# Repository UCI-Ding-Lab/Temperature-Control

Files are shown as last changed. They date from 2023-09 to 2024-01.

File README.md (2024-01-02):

# Ding Temperature Control
An accurate, customizable, and cost-effective temperature control system.
Please reach out to [UCI Ding Lab](https://www.ding.eng.uci.edu) for any questions or requests. 

The temperature control system is designed to maintain a stable temperature from room temperature to 60 °C within 0.06 °C. On the aluminum target block, two adhesive polyimide heating elements and two temperature sensors are attached on the side. These sensors and heating elements are connected to an Arduino Nano which controls the temperature output with an external 24V power supply using the PID algorithm. 

This GitHub repository includes the PCB KiCad and Gerber files, PCB enclosure Fusion 360 and STL files, and Arduino code.

### Major steps to build the system.
Protocol Graphical Abstract

## PCB
The PCB is designed in KiCad 6.0, in which users can edit the layout for free. It is a 2-layer board with all through-hole components. 
The top layer is a +5V plane and the back layer is a ground plane. 
It houses the Arduino Nano, female headers, DC barrel jack, and screw terminal jack.

### Layout of the PCB
Ding Temperature Control PCB Layout

### KiCad model of the PCB
Ding Temperature Control PCB Transparent

## Enclosure
The enclosure is designed in Fusion 360 with a top and bottom piece. It is designed to be printed on a 3D printer with PLA and without any support. 
It contains M3 threaded inserts to connect the PCB, LCD, and buck converter. 

A Fusion 360 model of the enclosure.
Ding Temperature Control Housing

## Arduino Code
The Arduino Nano on the PCB reads the temperature sensors and calculates the heating power to reach the target temperature with the PID algorithm. 
Then, a PWM signal is sent to the MOSFET with the heating elements to heat the target block.
The PID algorithm is implemented from [QuickPID](https://github.com/Dlloydev/QuickPID).

## Example Data
The temperature recording of 4 trials has been provided in an Excel workbook. 

Note: The probe temperature sensor sometimes read -127 °C. This is an expected behavior. The PID algorithm omits the sensor reading and uses the previous average temeprature to calculate power output.



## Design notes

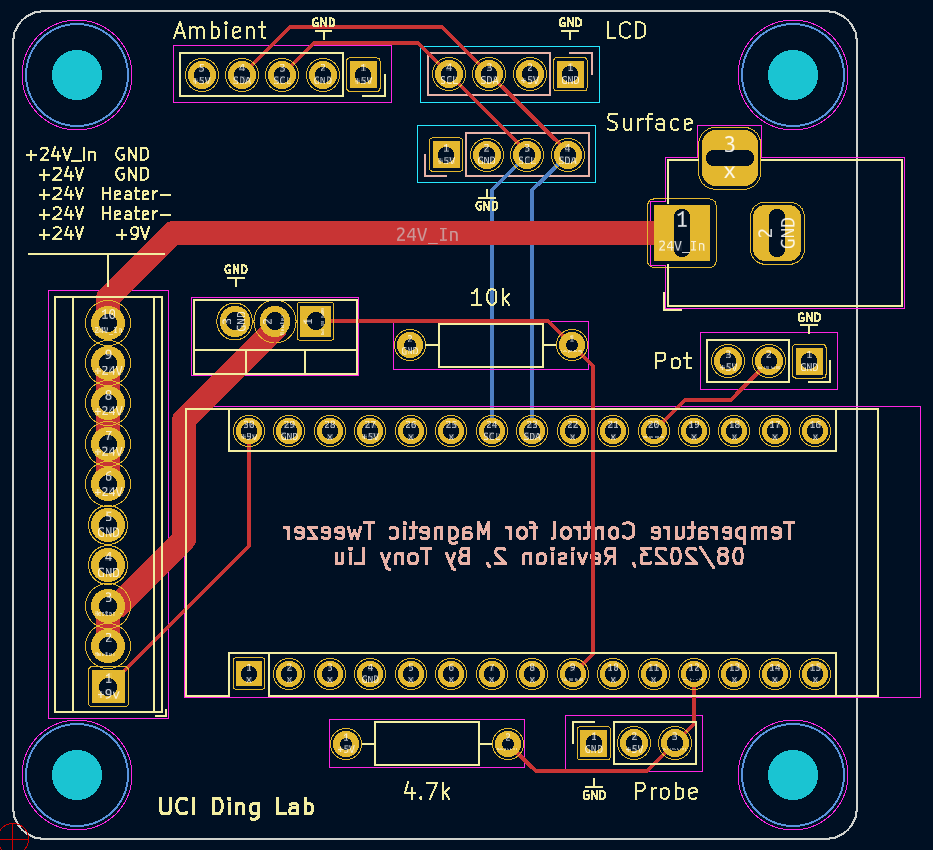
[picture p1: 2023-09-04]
PCB/Ding Temperature Control PCB Layout.png

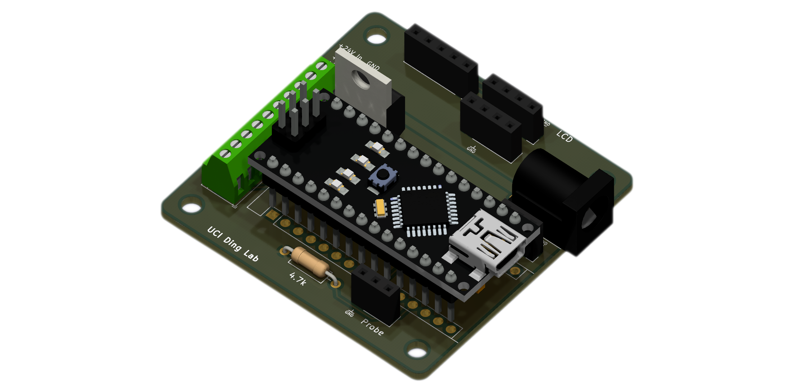
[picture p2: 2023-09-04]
PCB/Ding Temperature Control PCB Transparent.png

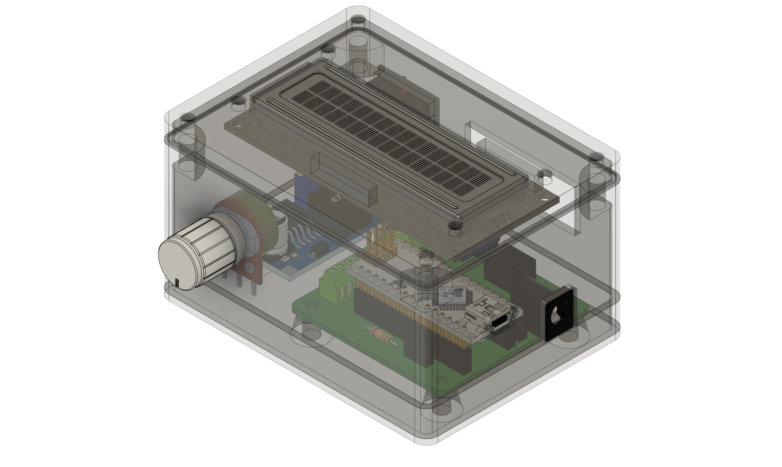
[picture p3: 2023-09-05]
Enclosure/Ding Temperature Control Housing.png

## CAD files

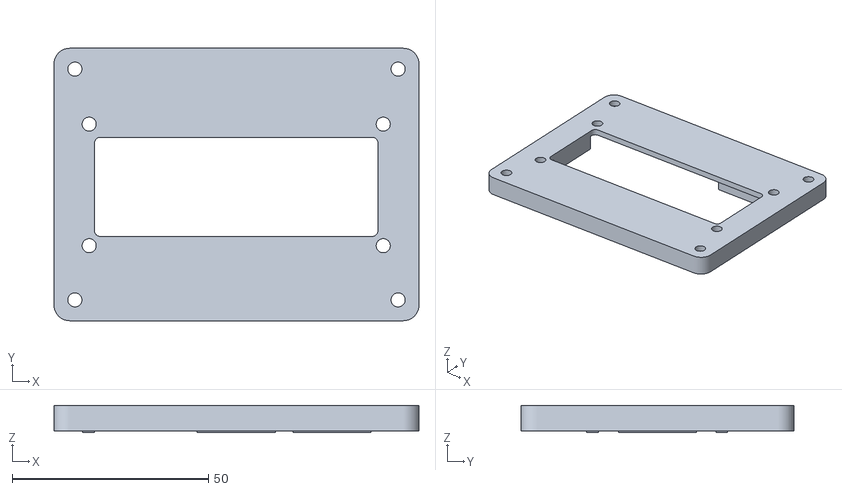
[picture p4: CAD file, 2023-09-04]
Enclosure/Enclosure Top.stl
93.1 x 69.5 x 6.90

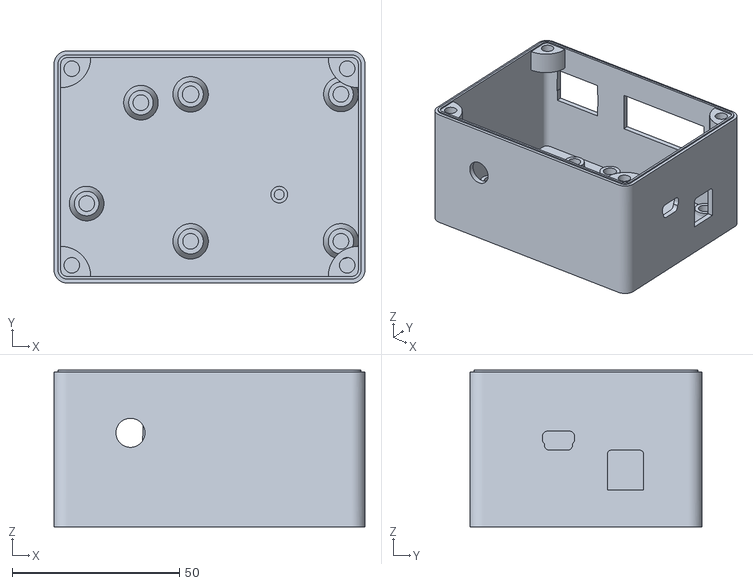
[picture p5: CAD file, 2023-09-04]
Enclosure/Enclosure Bottom.stl
93.1 x 69.5 x 46.9

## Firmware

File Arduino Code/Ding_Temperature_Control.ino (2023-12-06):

/********************************************************
   PID Temperature Control for Microscopes, Microfluidic Chambers, and Custom Incubators
   By: Tony Liu @ Ding Lab
 ********************************************************/

// Include libraries for sensors, LCD, and PID
#include <OneWire.h>
#include <DallasTemperature.h>
#include <Wire.h>
#include "Adafruit_MCP9808.h"
#include <LiquidCrystal_I2C.h>
#include <QuickPID.h>

// Declare physical pin numbers connected to the components
const int PROBEPIN = 9;
const int HEATERPIN = 6;
const int TARGETPIN = 1;

// Declare tempearture variables
float targetTemp, Input, Output;
double probeTemp, mcpTemp, mcpTemp2, avgTemp;

// PID constants; change these according to your setup in step 4
float Kp = 505, Ki = 62, Kd = 92;

// Constructors for sensors
OneWire oneWire(PROBEPIN);
DallasTemperature probe(&oneWire);
LiquidCrystal_I2C lcd(0x27,20,4);
Adafruit_MCP9808 mcp = Adafruit_MCP9808();
Adafruit_MCP9808 mcp2 = Adafruit_MCP9808();

// Create PID object from QuickPID library by David Lloyd 
QuickPID myPID(&Input, &Output, &targetTemp);

// Reads potentiometer (temperature control knob) input and converts to 20-60 Degree for the target temperature
void changeTargetTemp()
{
  // Read potentiometer input from 0 to 1023
  int targetInput = analogRead(TARGETPIN);

  // Converts potentiometer input to 20-60 degree target temperature
  targetTemp = map(targetInput, 0, 1023, 20, 60);
}

//Reads all temperature sensors and potentiometer
void readInput() 
{
  // Reads the target temperature from the potentiometer
  changeTargetTemp();

  // Prints the target temperature to the serial monitor
  Serial.print("Target:");
  Serial.print(targetTemp);
  Serial.print(" ");

  // Prints the target temperature to the top right of the LCD
  lcd.setCursor(9, 0);
  lcd.print("T:");
  lcd.print(targetTemp, 2);

  // Updates the temperature reading from the probe sensor, prevents unstable -127 readings
  probe.requestTemperatures(); 
  float probeReading = probe.getTempCByIndex(0);
  if(probeReading != -127.0)
    probeTemp = probeReading;


  // Prints the probe temperature to the serial monitor
  Serial.print("| Internal:");
  Serial.print(probeTemp, 3);
  Serial.print(" ");
  
  // Updates the temperature reading from the surface MCP sensor
  mcpTemp = mcp.readTempC();

  // Prints the surface MCP temperature to the serial monitor
  Serial.print("| Surface:");
  Serial.print(mcpTemp, 3);
  Serial.print(" ");
  
  // Updates the temperature reading from the ambient MCP sensor
  mcpTemp2 = mcp2.readTempC();

  // Prints the ambient MCP temperature to the serial monitor
  Serial.print("| Ambient:");
  Serial.print(mcpTemp2, 3);
  Serial.print(" ");
  
  // Prints the ambient MCP temperature to the bottom left of the LCD
  lcd.setCursor(0, 1);
  lcd.print("A:");
  lcd.print(mcpTemp2, 2);

  // Calculates the average temperature between the probe and surface MCP
  if(probeTemp > 15 && mcpTemp > 15) // Only calculates average if both sensors are above 15 degrees; prevents unstable readings
  {
    avgTemp = (probeTemp + mcpTemp) / 2.0;  
    Input = avgTemp;
    Serial.print("| Average:");
    Serial.print(avgTemp, 3);
    Serial.print(" ");
    
    // Prints the average temperature to the top left of the LCD
    lcd.setCursor(0, 0);
    lcd.print("I:");
    lcd.print(avgTemp, 2);
  }
}

// Setup function runs once at the beginning of the program
// Initializes sensors, LCD, and PID
void setup()
{  
  // Initialize serial monitor, LCD, and probe sensor
  Serial.begin(9600);
  while(!Serial);
  lcd.begin(16, 2);
  probe.begin();

  // Initialize MCP sensors; if not found, print error message and pause program
  if (!mcp.begin(0x18)) 
  {
    Serial.println("Couldn't find MCP9808!");
    while (1);
  }
  if (!mcp2.begin(0x19)) 
  {
    Serial.println("Couldn't find MCP9808 Number 2 (Ambient)!");
    while (1);
  }
  
  // Set MCP sensor resolution to 0.0625 °C
  mcp.setResolution(3);
  mcp2.setResolution(3);
  
  // Set heater and target pins to output mode
  pinMode(HEATERPIN, OUTPUT);
  pinMode(TARGETPIN, INPUT);
  
  // Initialize LCD and turn on backlight
  lcd.init();
  lcd.backlight();

  // Set initial target temperature to 25 degrees
  targetTemp = 25;

  // Apply PID gains
  myPID.SetTunings(Kp, Ki, Kd);

  // Turn the PID on
  myPID.SetMode(myPID.Control::automatic);
}

// Loop function runs repeatedly after setup
// During every loop, the program reads temperature, computes PID output, and writes to LCD
void loop()
{
  // Reads input, computes PID, and writes output
  readInput();
  myPID.Compute();
  analogWrite(HEATERPIN, Output);

  // Prints the output percentage to the bottom right of the LCD
  lcd.setCursor(9, 1);
  float outputPercent = Output/255*100;
  lcd.print("O:");

  // Adjusts the number of decimal places depending on the output percentage
  if(outputPercent == 100)
  {
    lcd.print(outputPercent, 0);
    lcd.print("% ");
  }
  else if(outputPercent < 10)
  {
    lcd.print(outputPercent, 2);
    lcd.print("% ");
  }
  else
  {
    lcd.print(outputPercent, 1);
    lcd.print('%');
  }

  // Prints new line to serial monitor to serperate each loop
  Serial.print("| Output:");
  Serial.print(outputPercent);
  Serial.println("%");

  // Delays for 100 ms to allow the algorithm and sensors to update
  delay(100);
}
